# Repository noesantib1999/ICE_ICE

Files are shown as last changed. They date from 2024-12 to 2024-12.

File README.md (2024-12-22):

# Robotic ICE Catheter
Testing of 2-DOF Robotic ICE Catheter Manipulator for Minimally Invasive, Intracardiac Surgery

## Overview 
### Background
Minimally invasive surgery (MIS) and robot-assisted surgery (RAS) are becoming more commonly used approaches to treat high-risk procedures due to their small-incision operation area, and enhanced precision and control, respectively. By combining these two methods together, you can get increased efficiency and effectiveness in various surgical operations. In cardiology, for example, they allow for reduced mortality rates, lower median length of stay, less blood transfusions, and decreased risks of infection across different studies.

MIS/RAS

Among the different areas in cardiology, echocardiography (or cardiac ultrasound) is one where RAS is still being  prototyped. Transesophageal echocardiography (TEE) in particular, a historically common MIS procedure for heart ultrasound through the esophagus, has been the main method used to develop robot-assisted techniques, with outcomes such as reduced radiation exposure, precise, flixible control, and low-latency teleoperations. However, intracardiac echocardiography (ICE) is currently the most adopted method for examining ultrasound due to its thin catheter profile and ability to traverse through the heart chambers. Moreover, compared to TEE, ICE procedures tend to result in shorter length of stay, reduced fluoroscopy and sedation, and closer field of view to desired heart regions. However, this approach is still novel in robotic integration, leaving an opportunity for development of an ICE robotically-assisted system.

ICE
### Goal
Design, build, and test a 2-DOF robotic mechanism adapter for effective navigation of an intracardiac echocardiography (ICE) catheter through a heart.
## Hardware
### Medical Equipment
- ACUSON Acunav 8F Ultrasound Catheter (for Siemens Systems) 
- ACUSON P500 Ultrasound System

### Electronics
- Teensy 4.0 w/ Micro-USB to USB cable
- 2 Miuzei High-Torque (25 kg*cm) Waterproof Servo Motors w/ cross-shaped servo arm
- Video capture unit (ex. ElGato HD60 X) w/ HDMI and USB connections
- Laptop w/ Python and Arduino/C++ coding software (x2 if using teleoperations)

### Other Materials
- 3D Printed Parts (PLA filament, 15% infill) - see CAD Designs folder for files
- AC-to-DC Power Supply (4.8-8.4 V Output)
- 2 D-Profile Rotary Shafts (1/2" Diameter, 6" Long, 1045 Carbon Steel) - McMaster number: 8632T134
- 4 Oil-Embedded Bronze Sleeve Bearings (5/8" Housing ID, 5/16" Long, for 1/2" Shaft Diameter) - McMaster number: 6391K736
- Breadboard
- Wires

## Assembly
### CAD Assembly:
The full assembly of the robotic ICE catheter is available when navigating to the CAD Designs folder, and into the "SolidWorks Files - Final" subfolder. Here, the different SLDPRT and SLDASM files that contribute to the complete 3D assembled view in SolidWorks can be located. The CAD Designs folder also has a "STL Files - Final" subfolder, which contains all the STL files needed for 3D printing, along with a short instruction set. You will need slicing software and a 3D printer, such as PrusaSlicer and the Prusa MK3S printer, respectively. Use PrusaSlicer to create a G-code for the STL files, and print each part from the G-code as required. Refer to the specifications in the short instruction set to ensure all parts are properly printed.

CAD_Assem

### Mechanical Assembly:
After printing, begin assembling the components. The Shaft_Support part is designed to connect two servos, while the ICE_Support_0000 serves to hold the ICE catheter. Position and secure the printed components to hold these parts in place. Ensure proper alignment and fit as per the CAD model.

Mech

### Electrical Assembly:
Wire the two Miuzei servos to the Teensy 4.0 as shown in the provided circuit diagram. Ensure all electrical connections are made securely, following the correct wiring paths for power and signal transmission between the components. Verify that all connections are stable and functional before proceeding to the next steps in testing and calibration.

circuit

On the breadboard, the arrangement should be as follows.

breadboard

## Firmware
Included in this repository are two scripts intended to be run on a Teensy 4.0 (or equivalent board with modifications). These scripts should be uploaded to the Teensy board using a serial USB connection via the Arduino IDE. Each script is also capable of, but does not necessarily require, two-way communication with a computer via this serial USB connection. The functionality and intended use cases of each script are detailed below.

### TEENSY INTERFACE
- Purpose: The TEENSY INTERFACE script directly controls the velocities of each servo for use in controlling ICE catheter manipulation. It is capable of receiving velocity commands over serial interface at 9600 baud. The script can be run in an emulation mode (defined by the variable "emulationMode") to simulate a series of potential velocity commands to each servo. 
- Instructions:
    - Setup:   Verify system definitions for servo positional travel limit and center position (refer to SERVO_CALIBRATION to verify these limits). We recommend using a center position of 135 and travel limit of 80 during typical operating conditions with a 1:1 servo gear ratio. 
    - General: Ensure that servos are connected to power and their respective pins. Connect the Teensy to a computer establishing a USB connection.
    - Use: 
        - Emulation true - The Teensy will not wait for nor respond to instructions though serial communications.
        - Emulation false - Individual servo velocities are controlled by the Teensy as directed by serial communication commands. 
        
### SERVO CALIBRATION
- Purpose: This script directly controls the positions of each servo for use in initial hardware assembly and troubleshooting. Servos are initially moved to "servo_center_pos" defaulting at 135 degrees (recommended). Script will then accept serial inputs to control servo position.
- Instructions: 
    - General:  Ensure that servos are connected to power and their respective pins. Connect the Teensy to a computer establishing a USB connection.
    - Use:      Prior to assembling the ICE hardware, ensure servos positions are set to 135 using this script and can otherwise move freely. Assemble servo gear interface with the ICE catheter in its home position (completely straight). Once assembled, ensure servos can spin by setting the position to a slightly different value using the above format. Progressively test values closer to both 0 and 270 and identify the furthest distance the servos can spin from the home position. Use this to update "servo_pos_limit" for both this script and "TEENSY_INTERFACE."

### Note on firmware commands via serial communication:
Commands must be passed to the Teensy as text strings with a format of either "Ax.x" or "Rx.x" where A and R refer to the antero-posterior and right-left catheter knobs to be controlled and x.x refers to any floating point number. Commands can either be sent through the Arduino IDE in the serial monitor or using the software GUI described below.

## Software
The objective for this part was to develop a graphical user interface (GUI) to enable intutive control of robot motion via the Teensy microcontroller. Taking this into consideration, the GUI would allow users to input desired velocities for two axes - Left/Right and Posterior/Anterior -, implementing a smooth gradual velocity adjustment to the desired location. Additionally, the GUI would have a coordinate system to click on and automatically guide the catheter through precise motion control.

### Graphical User Interface (GUI)
The purpose of this GUI is to enable users control of the robotic ICE catheter via serial connection. For starters, open GUI_Live.py and make sure that the microcontroller's serial USB connection is the same as the "port" value in line 11 of the code; if not, update it. Once updated, run the code in a Python programming software to open the GUI.

The GUI contains the following items:
- E-STOP button: located in the top left part of the screen in a bright red color, it serves as an override button and instantly changes the robotic ICE catheter's velocity vector to zero.
- Velocity update rate: placed below the E-STOP button to the left. With these three buttons, choose the velocity delay value, with the default value set as 10 (smallest is fastest).
- Instantaneous velocity scrollbars: with this input method, change the angular velocity rate instantly by moving the scrollbars, each labeled with their respective movement axis.
- Coordinate system: located below the button and scrollbars. Click on the coordinate system to change the velocity vector, moving the catheter at the desired rate.
- Live Ultrasound Feedback: located on the right side of the screen; a live image of the ultrasound can be displayed using VideoCapture() and through effective connection from the ultrasound viewing system to the main computer using a video capture unit.

GUI

### Teleoperations via UDP/Sockets

Two additional codes are also included in the Software folder, named Tele_GUI_Send.py and Tele_ICE_Receive.py, used for teleoperations with sockets and UDP packets. For this approach, use one computer as the "sender", which will run the Tele_GUI_Send.py code and utilize the GUI the same way as before to send the velocity vectors as UDP packets to the "receiver", another computer which runs the Tele_ICE_Receiver.py code and connects to the Teensy microcontroller via serial connection.
- Note: make sure both sets of code have the same gateway port number to ensure effective connection between the computers. Additionally, search for the receiver's IP address via "ipconfig" in your command window, and copy/paste the IPv4 address into the Tele_GUI_Send.py script in line 8.

## Experimental Setup

### In-Situ Testing 
InSitu

The experimental setup consisted of having the robotic ICE catheter connected to the ACUSON P500 system to get an ultrasound view of a human heart on the machine. To start, the P500 was connected via HDMI to a video capture unit, gathering the live ultrasound frame and sending it over to the main computer via USB connection. The image from the P500 would then show in the GUI program. 

- Note: The procedure can be replicated if the ICE catheter and ultrasound viewing system are compatible (both are from the same brand). Additionally, check whether the HDMI ports in the ultrasound system are IN or OUT, as video capture units tend to receive the image from OUT ports.

The TEENSY_INTERFACE.ino code is uploaded into the Teensy 4.0 microcontroller, and remains connected via USB to the main computer. After closing the Arduino IDE program, go to a Python prorgamming software, open GUI_Live.py, and run the GUI. After the GUI is opened, the ultrasound tip of the ICE catheter is inserted into the container with the human heart. From here, the catheter can be oriented through clicking on the coordinate system or the scrollbars in the GUI.

Movement of the catheter through the heart for this experiment is straightforward: the catheter will enter through the inferior vena cava (IVC) and examine the right atrium. Some movements with the GUI would be performed before moving forward to the right ventricle, where the experiment concludes.

### "Teleoperations" via video conferencing application
One extra step considered for a method of teleoperation is the use of video conferencing software. By having two computers access the same conference link, the main computer (connected to the Teensy 4.0) can grant desktop control to the external computer and the latter can guide the ICE catheter through the GUI program. 

VC_Tele

### UDP/Sockets Teleoperations
Using Tele_GUI_Send.py and Tele_ICE_Receive.py, the "sender" computer would run the GUI program, operate the controls, and send the infomation via UPD packets to the "receiver" computer, operating the robotic ICE catheter.

## Results
### In-Situ

The experiments were attempted on two different human hearts from the Visible Heart Lab's Heart Library. For Heart #1, placed in a small container with water, the catheter entered through the IVC and was able to reach the right atrium. However, after moving the catheter using the coordinate system of the GUI, the velocity vectors were be very high and prevented movement into the right ventricle. After using the scrollbars to manually control the servos and guide it to the right ventricle.

InSitu_Test

For Heart #2, the experiment was done in a wider container, which caused the heart to have less constrained movement and follow the displacement of the ICE catheter, affecting the ultrasound image result. After grabbing ahold of the heart, the movement of the ICE catheter performed similar to Heart #1.

Some considerations to add after this initial experimental setup is to set the heart in a static position in the container to have effective movement of the ultrasound tip through the heart chambers. Additionally, it is recommended that the velocity vectors are reduced to prevent any quick changes in movement inside the heart and affecting the patient, as well as having a position-based system for more effective ICE catheter orientation.

### "Teleoperations"

This approach was only tested in Heart #1. From the external computer, evident lag and low resoulution quality were found, making it challenging to move the scrollbars and observe the desired heart regions via the ultrasound. Although an effective proof of concept, it is recommended to consider other approaches. 

Zoom_tele

### Teleoperations

Due to time constraints, this approach was not yet tested in a human heart. However, teleoperation results showed low-latency communications between the two computers, making it an effective method for sending data over the internet to operate the robotic ICE catheter. One observation from these tests, nonetheless, is that when utilizing the scrollbars for changing the velocity vectors, the Tele_ICE_Receiver.py code waited for the main "sender" computer to stop sending data to ultimately perform the movement. Further examination is required to verify whether this approach is helpful or can place challenges when needing to send multiple data packets in a short time period.

Tele_Test

## Credits
ME 8284 - Intermediate Robotics with Medical Applications (Graduate-Level Course)

Team Prince: <br>
Team Manager - Noé Bazán (baznp001@umn.edu) <br>
Mechanical Leads - Anders Torp (gloeg011@umn.edu) and Rucha Pansare (pansa008@umn.edu)<br>
Embedded Lead - Michael Feldkamp (feldk066@umn.edu)<br>
Software Lead - Shrivatsa Deshmukh (deshm080@umn.edu)<br>
Floater - Tianning Li (li003291@umn.edu)

Presentation Link (from December 10th 2024): https://docs.google.com/presentation/d/189g-k64IC7r7hnKr-tXK-r5zNP0DUaRn04MexWa3yLw/edit?usp=sharing

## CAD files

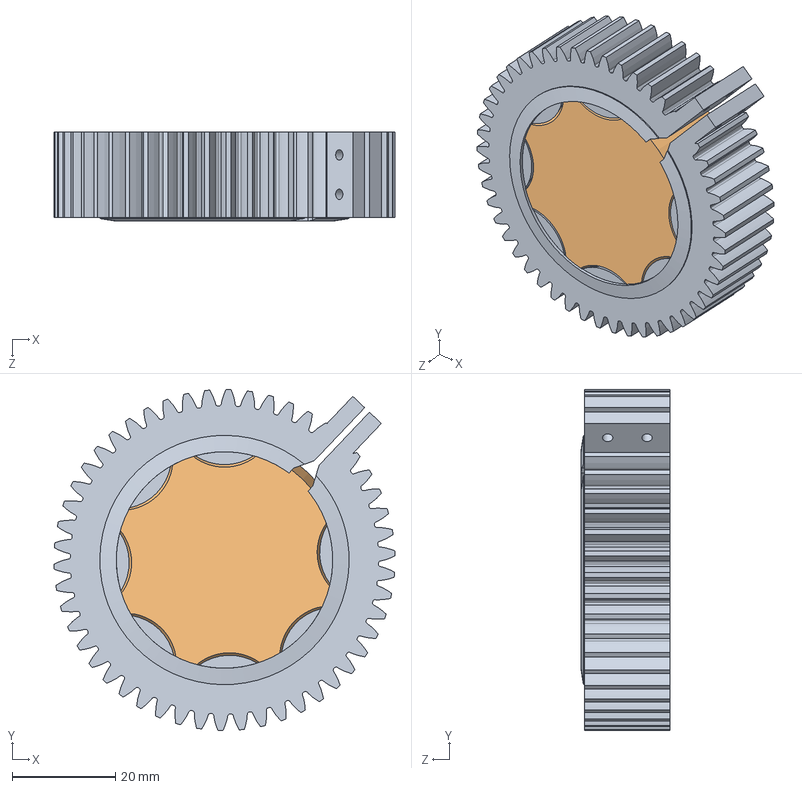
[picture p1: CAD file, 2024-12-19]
CAD Designs/SolidWorks Files - Final/PA_Gear_Assem.SLDASM
66.0 x 66.0 x 17.3 mm
ICE_PA_Knob
PA_Gear_BackLock

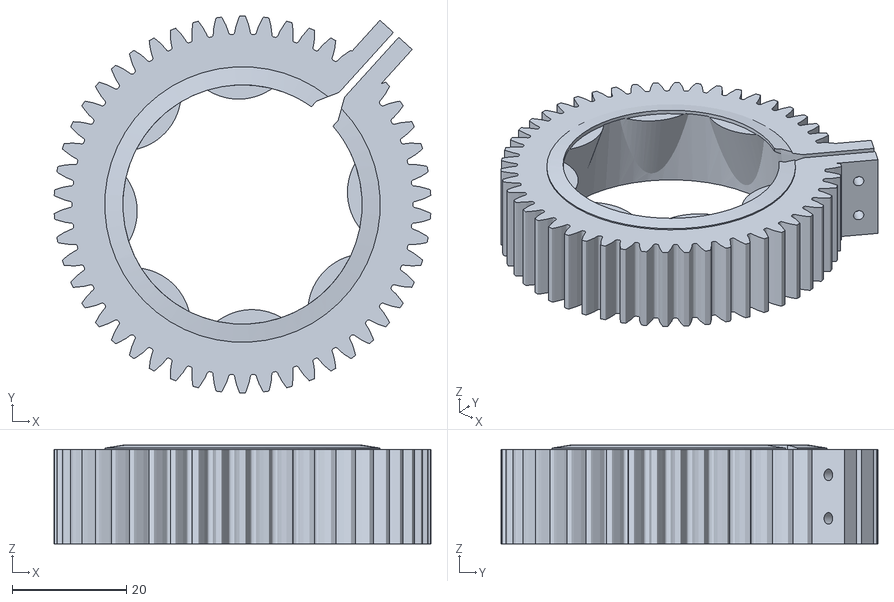
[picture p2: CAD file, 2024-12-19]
CAD Designs/STL Files - Final/PA_Gear.STL
66.0 x 66.0 x 17.3

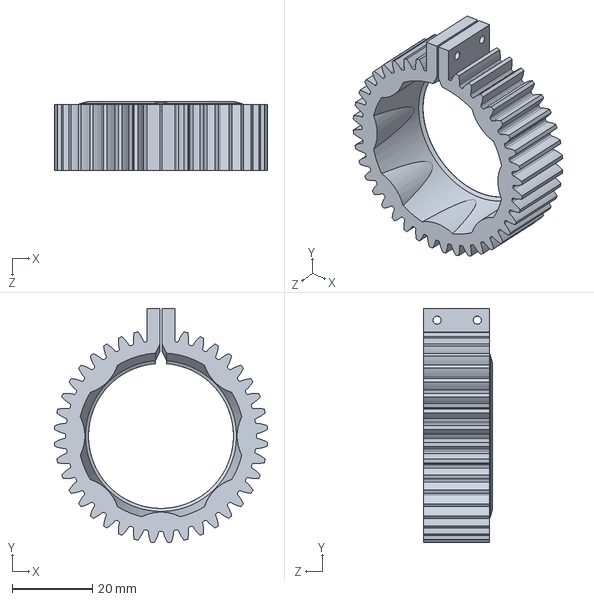
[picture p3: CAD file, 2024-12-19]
CAD Designs/SolidWorks Files - Final/LR_Gear.SLDPRT
53.2 x 58.5 x 17.3 mm

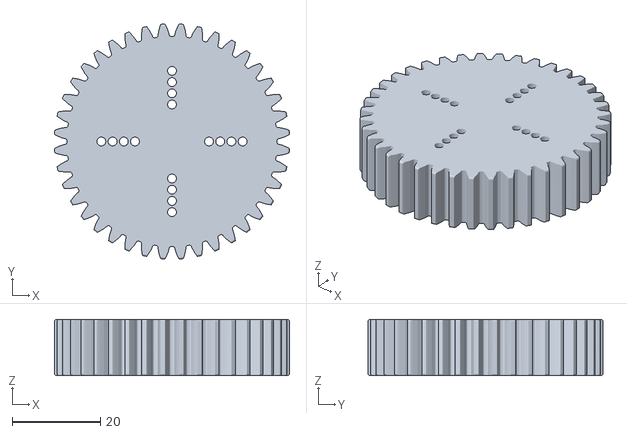
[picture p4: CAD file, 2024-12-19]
CAD Designs/STL Files - Final/LargeGear.STL
53.2 x 53.2 x 12.7

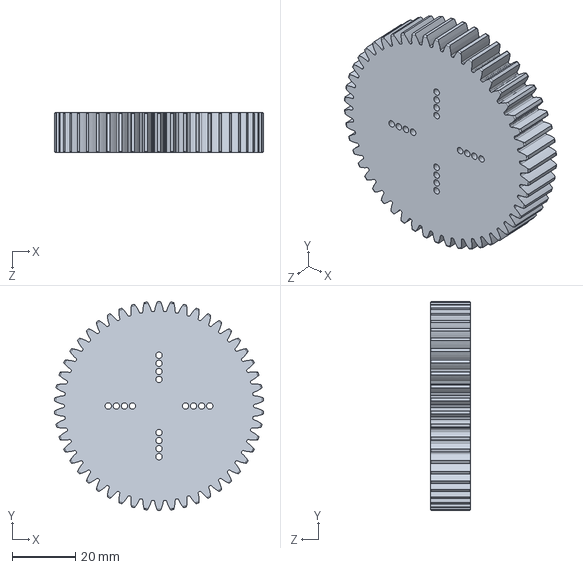
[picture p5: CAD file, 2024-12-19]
CAD Designs/SolidWorks Files - Final/EvenLargerGear.SLDPRT
66.0 x 66.0 x 12.7 mm

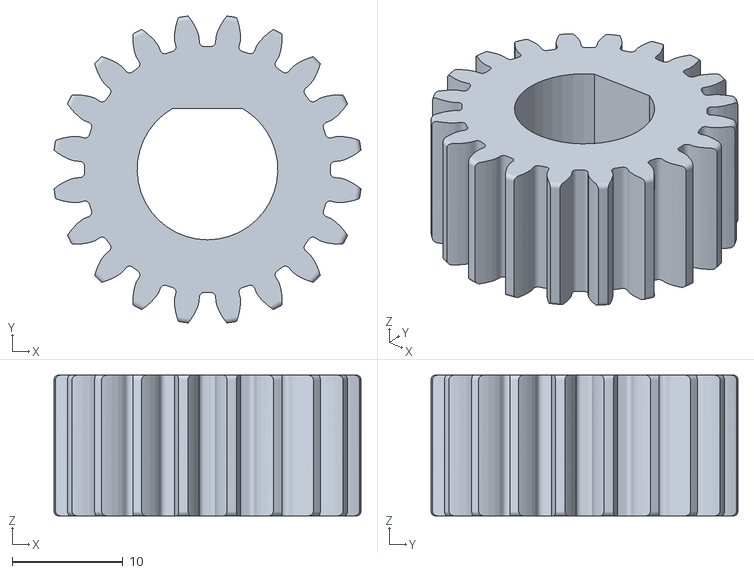
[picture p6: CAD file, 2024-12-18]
CAD Designs/STL Files - Final/SmallGear_0.50.STL
27.7 x 27.7 x 12.7

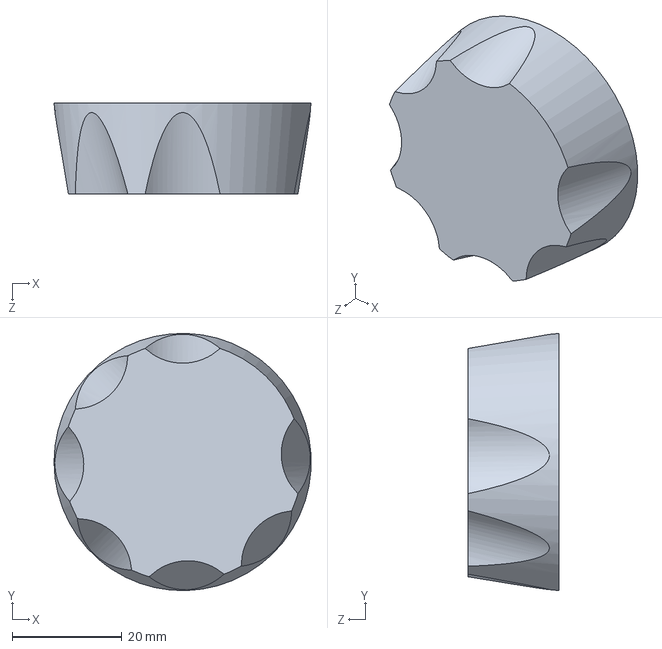
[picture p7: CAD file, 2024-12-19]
CAD Designs/SolidWorks Files - Final/ICE_PA_Knob.SLDPRT
46.8 x 46.8 x 16.6 mm

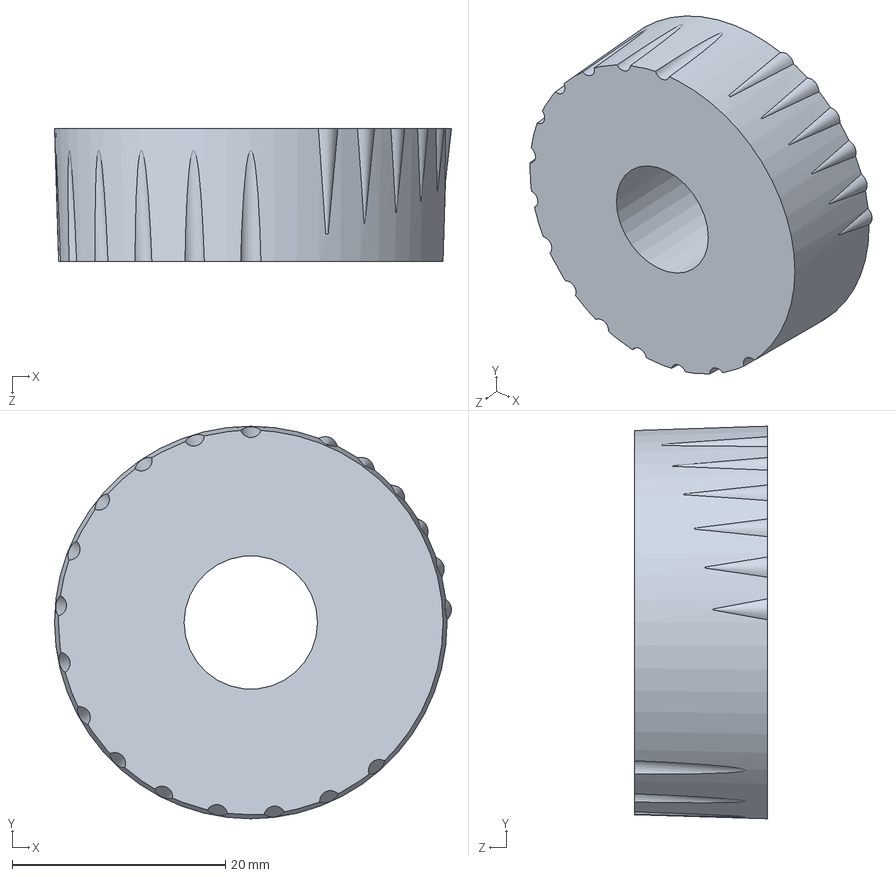
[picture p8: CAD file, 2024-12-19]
CAD Designs/SolidWorks Files - Final/ICE_Lock_System.SLDPRT
37.2 x 36.8 x 12.4 mm

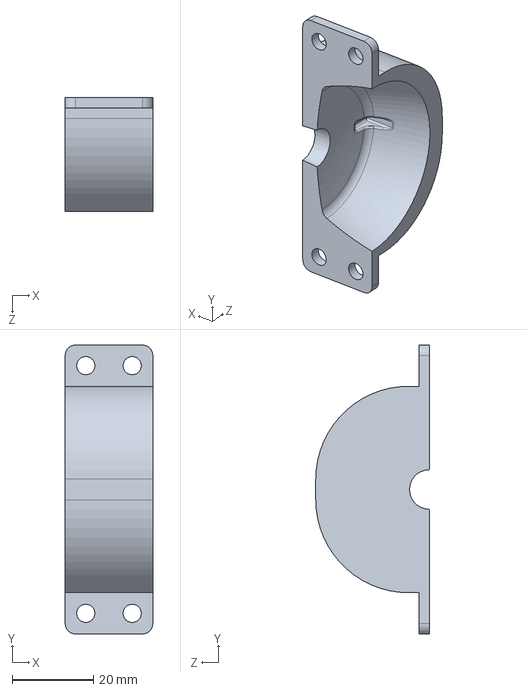
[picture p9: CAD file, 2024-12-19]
CAD Designs/SolidWorks Files - Final/ICE_Support_FrontTop.SLDPRT
21.6 x 71.1 x 27.9 mm

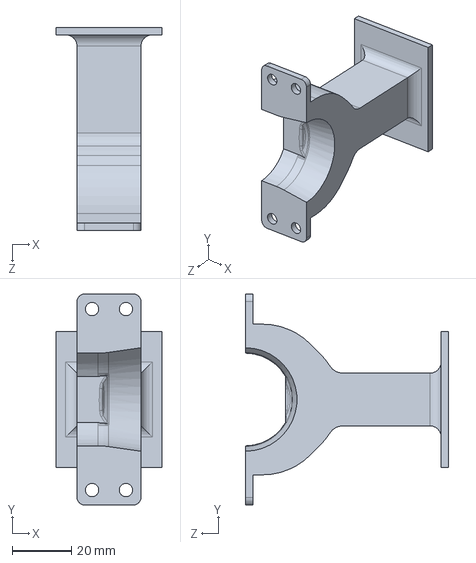
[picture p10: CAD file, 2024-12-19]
CAD Designs/SolidWorks Files - Final/ICE_Support_Back.SLDPRT
35.6 x 71.1 x 68.6 mm

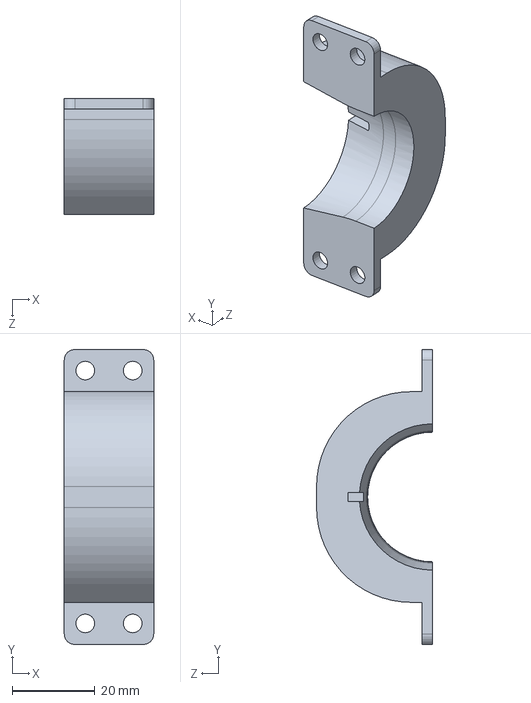
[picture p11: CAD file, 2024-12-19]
CAD Designs/SolidWorks Files - Final/ICE_Support_BackTop.SLDPRT
21.6 x 71.1 x 27.9 mm

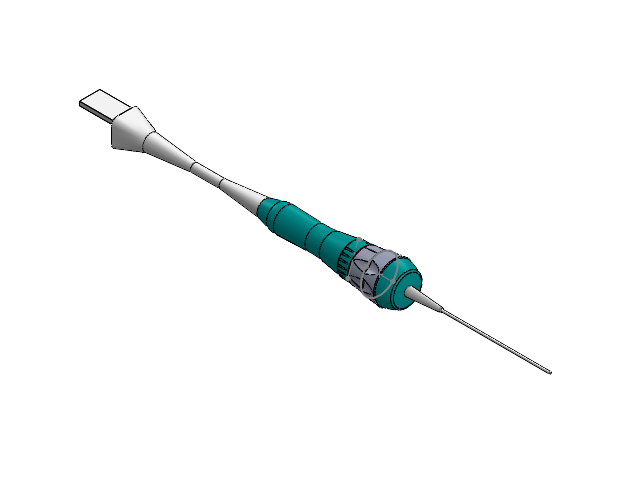
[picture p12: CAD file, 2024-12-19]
CAD Designs/SolidWorks Files - Final/ICE_Catheter.SLDASM
Handle
ICE_Lock_System
ICE_LR_Knob
ICE_PA_Knob

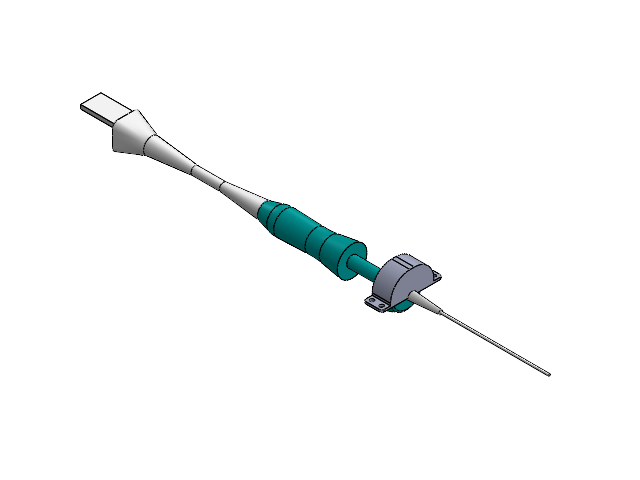
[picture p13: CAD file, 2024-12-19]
CAD Designs/SolidWorks Files - Final/Support_Assem_V1.SLDASM
Handle
ICE_Support_FrontTop

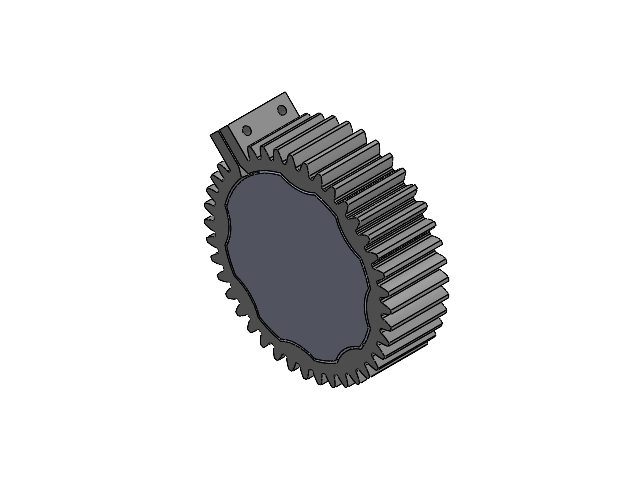
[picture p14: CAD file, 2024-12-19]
CAD Designs/SolidWorks Files - Final/LR_Gear_Assem.SLDASM
ICE_LR_Knob
LR_Gear

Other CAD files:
CAD Designs/SolidWorks Files - Final/CathAssem_Final.SLDASM
CAD Designs/STL Files - Final/SmallGear_0.51.STL
CAD Designs/STL Files - Final/SmallGear_0.52.STL
CAD Designs/SolidWorks Files - Final/PA_Gear_BackLock.SLDPRT
CAD Designs/Archived/6391K736_Oil-Embedded Bronze Sleeve Bearing.SLDPRT
CAD Designs/Archived/Casing.SLDPRT
CAD Designs/Archived/CathAssem.SLDASM
CAD Designs/Archived/CathHolder.SLDPRT
CAD Designs/Archived/IceCatheter_assemLR.SLDASM
CAD Designs/Archived/LargeGear.SLDPRT
CAD Designs/Archived/TopCathHold.SLDPRT
CAD Designs/STL Files - Final/EvenLargerGear.STL
CAD Designs/STL Files - Final/ICE_Support_Back.STL
CAD Designs/STL Files - Final/ICE_Support_BackTop.STL
CAD Designs/STL Files - Final/ICE_Support_Front.STL
CAD Designs/STL Files - Final/ICE_Support_FrontTop.STL
CAD Designs/STL Files - Final/LR_Gear.STL
CAD Designs/STL Files - Final/Shaft_Support.STL
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

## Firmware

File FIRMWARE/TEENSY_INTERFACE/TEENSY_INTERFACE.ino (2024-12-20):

/*
TEENSY INTERFACE SCRIPT - Michael Feldkamp, ME 8284, Originally written December 2024
GITHUB: https://github.com/noesantib1999/ICE_ICE
Purpose: This script directly controls the velocities of each servo for use in controlling ICE catheter manipulation. It is capable of receiving velocity commands over serial interface at 9600 baud.
         The script can be run in an emulation mode to simulate a series of potential velocity commands to each servo.
Implementation: Servos are initially moved to "servo_center_pos" defaulting at 135 degrees and run through a short series of positional commands to ensure proper working condition. 
                Script will then accept serial inputs to control servo VELOCITY via the following format:
                "Axx" will set the Anterior-Posterior (AP) servo to rotate at the float value xx in degrees/sec.
                "Ryy" will set the Left-Right (LR) servo to rotate at the float value xx in degrees/sec.
                Should accept only one input at a time. Any other input formats will be ignored.
Instructions: 
  Setup:   Verify system definitions for servo positional travel limit and center position (*refer to "SERVO_CALIBRATION" to verify these limits).
  General: Ensure that servos are connected to power and their respective pins. Connect the Teensy to a computer establishing a USB connection.

*/



#include <Servo.h>

// Pin definitions:
#define servo_AP_pin 14
#define servo_LR_pin 15

// System definitions:
#define servo_pos_limit 80 // Maximum amount servo should turn in a given direction in degrees, max is 135
#define servo_center_pos 135 // Servo position when catheter is straight

Servo servo_AP;
Servo servo_LR;

bool emulationMode = false; // When true, will not attempt serial connection and will go through some set commands
                            // When false, will connect to serial and receive/plot commands/values
        int loopstate = 0;  // Ignore if not running emulation mode

float cmd_Vel_AP = 0; // Units of degrees per second
float cmd_Vel_LR = 0;

float cmd_Pos_AP = servo_center_pos; // Units of degrees. Set to center_pos so the code starts it here.
float cmd_Pos_LR = servo_center_pos;

unsigned long t0 = micros();
unsigned long t_loop = 0;
unsigned long t_total = 0;
unsigned long t_cycle_0 = 0;

float setServoPos(Servo &servoObj,float cmdPos){
  //cmdPos is in degrees. This needs to be constrained and then remapped to microseconds
  float cmdPos_constrained = constrain(cmdPos,servo_center_pos-servo_pos_limit,servo_center_pos+servo_pos_limit); //Constrains the command degrees to center +- limit
  int cmdPos_micros = map(cmdPos_constrained,0, 270, 500, 2500); // The servo operates between 0 and 270 degrees for 500-2500 microseconds
  servoObj.writeMicroseconds(cmdPos_micros); // Using microseconds instead of regular servo.write() due to servo functionality;
  return cmdPos_constrained; // Rewrite the command position to the constrained position.
}

void handleSerialOutput(float cmd_Vel_AP, float cmd_Pos_AP, float cmd_Vel_LR, float cmd_Pos_LR, float t_loop)
{
  Serial.print("AP_Vel:"); Serial.print(cmd_Vel_AP); Serial.print("\n");
  Serial.print("AP_Pos:"); Serial.print(cmd_Pos_AP); Serial.print("\n");
  Serial.print("LR_Vel:"); Serial.print(cmd_Vel_LR); Serial.print("\n");
  Serial.print("LR_Pos:"); Serial.print(cmd_Pos_LR); Serial.print("\n");
  Serial.print("T_loop:"); Serial.print(t_loop); Serial.print("\n");
  Serial.println("________________________________________");
}

void handleSerialInput(float* cmd_Vel_AP, float* cmd_Vel_LR){
  while ( Serial.available() ){
    int inByte = Serial.read();
    switch (inByte) {
      case 'A':
        *cmd_Vel_AP = Serial.parseFloat();
        Serial.print("AP set to "); Serial.print(*cmd_Vel_AP); Serial.print("\n");
        break;
      case 'R':
        *cmd_Vel_LR = Serial.parseFloat();
        Serial.print("LR set to "); Serial.print(*cmd_Vel_LR); Serial.print("\n");
        break;
      default:
        Serial.println("ERROR: Failed to parse input");

    }
  }
}

void setup() {
  servo_AP.attach(servo_AP_pin,500,2500);
  servo_LR.attach(servo_LR_pin,500,2500);

  if (!emulationMode){
    Serial.begin(9600);
    Serial.println("Serial connected, running simple servo commands...");
    delay(500);
  }

  //Run servos through small commands to ensure hardware is connected and working.
  float temp_Pos_AP; // 
  float temp_Pos_LR;

  temp_Pos_AP = setServoPos(servo_AP, servo_center_pos+10);
  temp_Pos_LR = setServoPos(servo_LR, servo_center_pos+10);
  //  if (!emulationMode) handleSerialOutput(0, temp_Pos_AP, 0, temp_Pos_LR, 0);
  delay(500);
  temp_Pos_AP = setServoPos(servo_AP, servo_center_pos);
  temp_Pos_LR = setServoPos(servo_LR, servo_center_pos);
  //  if (!emulationMode) handleSerialOutput(0, temp_Pos_AP, 0, temp_Pos_LR, 0);
  delay(500);
  temp_Pos_AP = setServoPos(servo_AP, servo_center_pos-10);
  temp_Pos_LR = setServoPos(servo_LR, servo_center_pos-10);
  //  if (!emulationMode) handleSerialOutput(0, temp_Pos_AP, 0, temp_Pos_LR, 0);
  delay(500);
  temp_Pos_AP = setServoPos(servo_AP, servo_center_pos);
  temp_Pos_LR = setServoPos(servo_LR, servo_center_pos);
  //  if (!emulationMode) handleSerialOutput(0, temp_Pos_AP, 0, temp_Pos_LR, 0);
  delay(500);

  if (!emulationMode){
  Serial.begin(9600);
  Serial.println("Listening to serial input\n");
  Serial.clear();
  delay(500);
  }

}


void loop() {
  t0 = micros();

  if (!emulationMode)
  {
     handleSerialInput(&cmd_Vel_AP, &cmd_Vel_LR); 
  } else {
    t_total = micros()-t_cycle_0;
    if (t_total>=3000000) { // Cycle switches every 3 seconds
      t_cycle_0 = micros();
      loopstate = (loopstate+1)%4; // there are 4 cycle states
      // Serial.println(loopstate);
    }

    switch (loopstate) {
      case 0:
        cmd_Vel_AP = 10;
        cmd_Vel_LR = 10;
        break;
      case 1:
        cmd_Vel_AP = 20;
        cmd_Vel_LR = 20;
        break;
      case 2:
        cmd_Vel_AP = -10;
        cmd_Vel_LR = -10;
        break;
      case 3:
        cmd_Vel_AP = -20;
        cmd_Vel_LR = -20;
        break;
    }
    // low speed for 3 seconds, higher speed for 3 seconds, then switch and do the same in reverse
  }

  delay(10); // Very important - The main loop runs very fast (several us), so this slows it down to a reasonable refresh rate.

  // This block adds a step to the command position dictated by the command velocity
  float cmd_step_AP = cmd_Vel_AP*t_loop/1000000; //dx = dx/dt * dt
  float cmd_step_LR = cmd_Vel_LR*t_loop/1000000;

  cmd_Pos_AP = cmd_Pos_AP+cmd_step_AP;
  cmd_Pos_LR = cmd_Pos_LR+cmd_step_LR;

  cmd_Pos_AP = setServoPos(servo_AP, cmd_Pos_AP); // If the resulting command position fell outside the range, it will be rewritten here. Otherwise it's identical.
  cmd_Pos_LR = setServoPos(servo_LR, cmd_Pos_LR);

  if (!emulationMode) handleSerialOutput(cmd_Vel_AP, cmd_Pos_AP, cmd_Vel_LR, cmd_Pos_LR, t_loop); // Comment this out to not get bombarded with numbers

  t_loop = micros()-t0;
}

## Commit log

2024-12-04 Firmware added
    Fixed serial input issue where it was not recognizing RXX commands.
    Changed loop time to microsecond units instead of milliseconds. Depending on performance might change back.
    Changed cycle velocity and pattern in emulation mode so we test out different velocities for longer periods of time.
2024-12-06 Firmware updates
    Added a calibration code that the hardware team should use when assembling the servos on the catheter. Updated the servo center and limit values in both this and the original controller script to ref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
2024-12-07 Live fixes
    Made adjustments to code with servo attached to Teensy. Mainly fixed cycle logic as it was not working as intended.
2024-12-17 Archived CAD upload
    Adding initial 1-DOF design of robotic ICE catheter adapter.
    [8632T134_D-Profile Rotary Shaft.SLDPRT, Casing.SLDPRT, CathAssem.SLDASM, CathHolder.SLDPRT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]
2024-12-17 Archived CAD design upload
    [6391K736_Oil-Embedded Bronze Sleeve Bearing.SLDPRT]
2024-12-18 Add files via upload
    STL files for the final design
    [ICE_Support_Back.STL, ICE_Support_BackTop.STL, ICE_Support_Front.STL, ICE_Support_FrontTop.STL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]
2024-12-19 Final STL files
    [EvenLargerGear.STL, ICE_Support_Back.STL, ICE_Support_BackTop.STL, ICE_Support_Front.STL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]
2024-12-19 Create Assembly Info text
2024-12-19 Final Robotic ICE Catheter Design
    [6391K736_Oil-Embedded Bronze Sleeve Bearing.SLDPRT, 8632T134_D-Profile Rotary Shaft.SLDPRT, CathAssem_Final.SLDASM, EvenLargerGear.SLDPRT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]
2024-12-20 CAD Design Folder - all files in respective subfolders
    [SmallGear_0.52.STL]
2024-12-20 Minor fixes
    Adjusted delay times and servo limits.
2024-12-22 Update README: UDP/Socket Teleoperations and Team Credits/Slides
